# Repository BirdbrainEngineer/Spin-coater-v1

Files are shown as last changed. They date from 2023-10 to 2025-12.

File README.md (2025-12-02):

# Birbrain's DIY Spin Coater version 1
This repository contains the source code for a diy spin coater I designed. A video on YouTube showing some of the design- and build process of this device can be found [here](https://www.youtube.com/watch?v=mm2ZiJNfISs). 

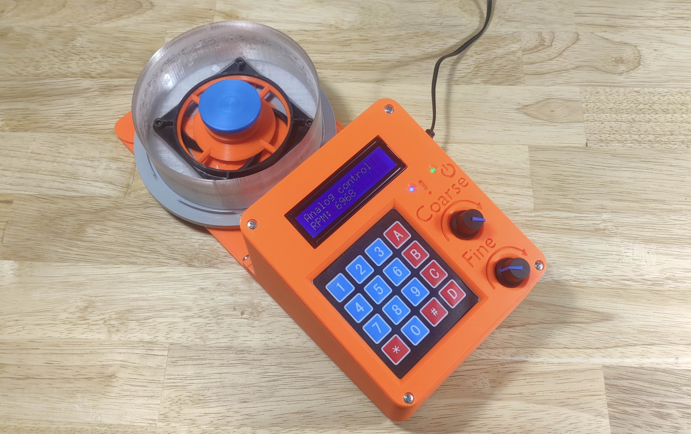
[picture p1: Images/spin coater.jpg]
Birdbrain's DIY Spin Coater version 1


### What is it?
 A spin coater is a tool used for depositing thin films of liquids onto a substrate. Usually the liquid is a solution of a relatively quickly evaporating solvent and the coating solute. The phantom force of centrifugal force causes any liquids to travel radially outwards on the substrate. However, due to surface tension, viscocity and other phenomena, some of the solution sticks to the substrate. The solvent from the thin layer of solution then evaporates, leaving behind a thin film of the solute. Using this technique, it is possible to obtain film thicknesses as small as a couple-dozen nanometers!
 
  So... in a nutshell, a spin coater is essentially just a controllable/programmable spinner onto which one can attach a variety of substrates. 
 
### Why?
 Due to the insane simplicity of this device, one would imagine that such tools would be rather cheap and easy to aquire... However, because usually these devices are used in universities and research laboratories, then unfortunately one can expect a markup in the hundreds, to sometimes thousands of percentage points!!! This is just pure insanity, and because I like building some of my own tools, I decided to design and build my own simple spin coater.

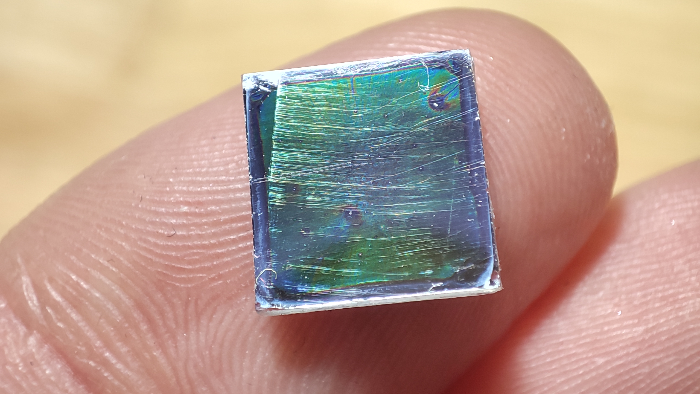
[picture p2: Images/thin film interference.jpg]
Thin film interference
 
 Above is a photo showing thin-film-interference on a coated first-surface mirror(definitely not optical quality haha). The coating solvent was acetone and solute was acrylic, which is a very challenging mix to work with... hence the somewhat sub-par result. 

### Is this project going to be maintained? 
 Don't hold your breath for it! I may upload a few bug fixes if and when they pop up as I work with my spin coater, but I do not intend to improve this version much if at all. There is a likelyhood that a few years from now, I will build a yet more advanced version- a spin coater of laboratory quality for projects that require utmost precision. 

### What is needed to build this project?
The spinner hardware is controlled by a Raspberry-Pi Pico(just Pico from here on), a cheap microcontroller that sits between an Arduino and ESP32 in its processing power. The speed of the Pico as well as its powerful hardware-PWM capabilities are the reason for me picking the Pico for this project.

Multiple extremely important parts of the device, such as the hub and sample holder combo that makes up the gravity chuck design of this spin coater, are meant to be 3d-printed. So, it is basically a necessity to have access to a basic 3d printer... or a cnc mill if going overkill. 

Because I did not make a PCB design for the logic board for this project, then you'll also need access to a soldering station.

And of course, a PC of some sort to be able to compile- and upload the firmware onto the Pico. More on software at [software setup](#software-setup) paragraph of this document.

The list of parts along with their approximate cost can be found at [bill of materials](#bill-of-materials) section of this document. 

## Software setup
This project uses [PlatformIO](https://platformio.org/) with [Visual Studio Code](https://code.visualstudio.com/)(VSCode) IDE. This near-trivializes certain aspects of programming for the Pico. In addition, this project uses the "earlephilhower" Arduino-pico core (see platformio.ini). For these reasons, as far as I am aware, the code is not possible to compile with any other setup, and even if it is possible, I recommend VSCode with PlatformIO anyways. Because the code uses a couple external libraries that PlatformIO normally manages, then it is necessary to have an Internet connection while dealing with this code. 

Getting the firmware for the Pico running should be as simple as these three steps. 

1. Clone the repository to your desired location and open the project in VSCode.
2. Connect the pico to your machine over a usb cable, while holding down the "BOOTSEL" button on the Pico. Release the BOOTSEL button after the Pico is connected.
3. Click "Build" and then "Upload" in VSCode, or just "Upload"(this should automatically build the project). The firmware should then be compiled and uploaded to the Pico. Once VSCode signals to you that the upload is complete, simply unplug the USB from the Pico and on the next power-up of the Pico, it should execute the code of the firmware.

Granted that the rest of the surrounding hardware has been built and set up correctly, the spin coater should just simply work. Surrounding hardware specification can be found under the "[Hardware design](#hardware-design)" paragraph of this document.

## Bill of materials
The prices in the bill of materials are approximate prices of the components that I could quickly find at the time of publishing of this document. These prices are most certainly subject to change over time.

* Anything in brackets is the particular size/component I used.
* Price is for the full amount (eg. 2$ for a component that has 4 stated in the amount, means each component costs 0.50$). 

| Amount | Component                                    | Price  |
|--------|----------------------------------------------|--------|
| 1      | Raspberry Pi Pico                            | 5$     |
| 1      | 80mm 4-pin PC fan (Arctic P8 Max)            | 10$    |
| 1      | 12V, 1A, power adapter with barrel connector | 5$     |
| 1      | SPI micro-SD-card reader module              | 3$     |
| 1      | 16x2 LCD display module                      | 4$     |
| 1      | 4x4 membrane keypad                          | 5$     |
| 1      | 15x21mm KCD1 power switch                    | 1$     |
| 1      | Suitable DC-005 barrel jack (5.5x2.1mm)      | 1$     |
| 4      | Suitable anti-slip rubber furniture leg      | 2$     |
| 1      | 25x (empty) cd/dvd spindle                   | 3$/10$ |
| 2      | WH148 10K potentiometer                      | 2$     |
| 2      | WH148 potentiometer knob                     | 2$     |
| 2      | PT15 10K potentiometer or equivalent         | 0.50$  |
| 12     | 3mm M3 heat set insert                       | 1$     |
| 4      | 4mm M4 heat set insert                       | 1$     |
| 2      | TO220 heatsinks                              | 1$     |
| 16     | M3 10mm screw                                | 0.50$  |
| 4      | M4 20mm or 17mm screw*                       | 0.50$  |
| 1      | 12x8cm prototyping/perf board                | 0.50$  |
| 1      | 1A glass tube fuse                           | 0.50$  |
| 1      | glass tube fuse holder                       | 0.50$  |
| 1      | 1N5819 schottky diode or equivalent          | 0.50$  |
| 5      | 1N4005 diode or equivalent                   | 1$     |
| 2      | 3mm round LED, different colors              | 0.50$  |
| 6      | resistors: 1x1K, 1x4K7, 1x6K8, 2x10K, 1x68K  | 0.50$  |
| 4      | 100nF ceramic capacitor                      | 0.50$  |
| 1      | 330nF 15V+ capacitor(I used 1x100nF, 1x100uF)| 0.50$  |
| 2      | 100uF 15V+ electrolytic capacitor            | 0.50$  |
| 2      | 2N2222A transistor or equivalent             | 0.50$  |
| 1      | F9540N transistor or equivalent              | 1$     |
| 1      | L7805CV voltage regulator                    | 1$     |
| -      | Preferred connectors & wiring for soldering  | ~5$    |
| -      | ~235g of PLA filament                        | 7$     |
| -      | ~42g of PETG filament                        | 1.50$  |

* Total: ~69$

## Hardware design
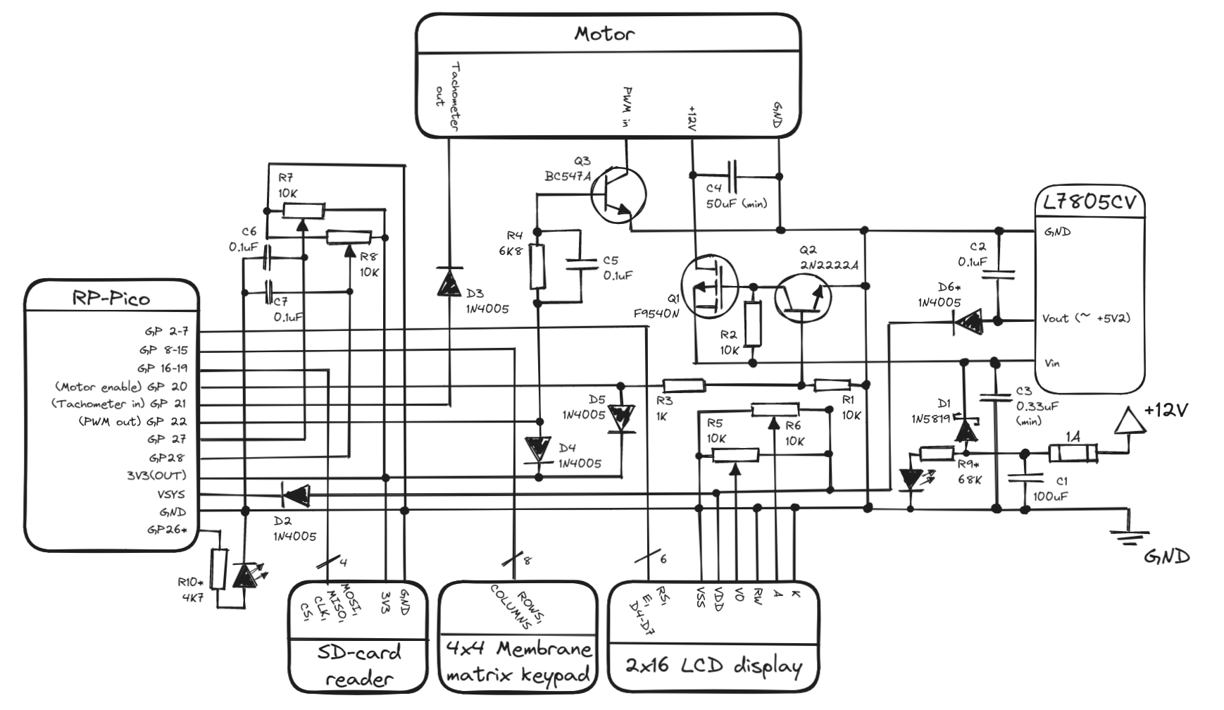
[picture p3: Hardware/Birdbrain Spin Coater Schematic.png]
Schematic


* Parts with a "*" are technically optional, but recommended. LED-s following a resistor with a * are optional in the same manner. 
* Q3 transistor in the schematic is a BC547A, however this can be replaced with a 2N2222A or equivalent. BC547A is an old and deprecated NPN BJT. The reason why I used it is to have a slower signal fall time (yes, really), which helps to make the PWM duty-cycle look more like what the Pico outputs. With a 2N2222A transistor, the PWM duty cycle to the fan motor is shorter than what the Pico outputs. Technically it should be fine as the PID control loop should be able to compensate.
* R5 & R6 are PT15 type potentiometers. R7 & R8 are WH148 type potentiometers.
* All 1N4005 diodes could technically be replaced by 1N5819 schottky diodes, but should not be necessary. 
* C3 capacity comes from the datasheet for L7805CV, however it does appear that the capacity can be larger. Probably the more important thing is that at least some of the capacity is quick-acting, eg. ceramic capacitors. 

### Some notes on the design...
If you would prefer to use a KiCAD schematic, then one has been produced and tested by @krasimirk. It can be found in the [BirdbrainSpinCoaterPCB_v1.1 directory](Hardware/BirdbrainSpinCoaterPCB_v1.1).

Make sure to install a TO-220 heatsink at least on the L7805CV, it will burn out otherwise. A heatsink on the F9540N is technically not needed, but optional.

One might notice that the 16x2 LCD display is directly interfaced with the Pico, even though the LCD display is running off 5V. This is safe to do as long as RW is tied to ground, guaranteeing that the display only ever gets written to. In such a case, the Pico's 3.3V should be enough to count as a logical high while transmitting data. 

## Spinner usage
If you have built yourself a spin coater of this design and firmware then here's a rundown of what can be found in the menu system of the spinner and what the different options do. 

### Keys
By default the keymapping for the spin coater when using the default 4x4 membrane keypad is as follows:

* Numerics - Correspond to the corresponding number. 
* `*` - Backspace / Exit.
* `#` - Enter / OK.
* `A` - YES, if a question prompt appears; Otherwise the letter A.
* `B` - NO, if a question prompt appears; Otherwise the letter B.
* `C` - UP, if navigating the menus; Otherwise the letter C.
* `D` - DOWN, if navigating the menus; Decimal dot/period ( `.` ), if entering a fractional number; Otherwise the letter D. 

### Booting
*For a painless first boot of the spin coater, make sure to copy the contents of the "Spinner Memory Image" folder onto a clean SD card. Ideally the SD card has a relatively small memory size.*

During booting, the spin coater checks for whether an SD card can be found on the default SPI pins. If not, then the spin coater will enter [memoryless operation](#memoryless-operation), and notifies the user of this occuring. The menu should then appear and the spin coater is ready for use in memoryless operation mode. 

If the SD card is present, then next the spin coater will check whether a `JOBS` folder exists in the root directory of the SD card. If not, one will be created automatically. If the `JOBS` folder exists, then the spin coater will attempt to load any jobs in the folder. The `JOBS` folder should contain *only* job files. [Job files](#job-file-structure) are extensionless JSON files with a very specific structure. Errors during this phase of booting could end up being unrecoverable AND recurring. If this is the case, the spin coater should be shut down, after which the SD card has to be removed from the spin coater and the files inspected at a PC. Any job files that have been saved incorrectly should be deleted from the folder. The spin coater should be able to boot again after doing so. 

Next the spin coater will attempt to locate the PID test job file called `PID` in the root directory. If this job is not found or is corrupted, then the spin coater will not be able to use the "PID test" functionality. In case of this happening and the user still wanting to use the PID test functionality, the user should shut down the spin coater, then remove the SD card from the spin coater and inspect the files at a PC. If a file called `PID` exists in the root directory then the integrity of the file should be checked, or alternatively a new PID test job file should replace the corrupted one. If the file is missing then a job has to be created/copied, and the file renamed to `PID`. 

### Normal operation
* `1/5: Quick start`
    * `1/2: Programmed` - Opens up a standard [job routine creation](#job-routine-creation) dialouge. After the dialouge has been finished, asks whether to run the job or not. If answered affirmatively, then executes the programmed job routine. After the routine has finished, asks whether to run the job again or not. If answered affirmatively, runs the job again. Otherwise asks whether to store the job permanently. If answered affirmatively, then a job name can be entered and the job routine will be saved as a job that can be interacted with through the `Jobs` menu.  
    * `2/2: Analog` - Gives direct control over the spinner to the user. The speed can be adjusted using the "coarse" and "fine" potentiometers. Coarse control spans from 0% to 90% of maximum spinner speed. Fine control spans a 10% range that gets added ontop of the current coarse control. Eg. if coarse control is set to 38% and fine control to 4%, then the output speed will be 42% of the maximum spinner speed. **WARNING: When exiting analog control mode, the spinner spins up to a slow speed for a few seconds, even if the spinner is already stationary!**
* `2/5: Jobs`
    * `1/3: Load job` - Opens a list of jobs currently stored on the SD card. The specific job can be searched in the menu, or by using the `Search for a job` function. If the job search turns up positive or the specific job is chosen from the menu, the spin coater asks whether to run the job. If answered affirmatively, performs the job routine. 
    * `2/3: Create job` - First asks to enter the new job routine's name. If a job with the specified name already exists, then offers to enter a different name or delete the job with the specified name. Once a suitable name is chosen, the spin coater asks to confirm the name, after which the standard [job routine creation](#job-routine-creation) dialouge is opened. After the job routine is finished, the job is saved on the SD card. If the user decided to override a previous job, then the previous job with the same name is deleted before the new job is saved. 
    * `3/3: Delete job` - Opens a list of jobs stored on the SD card. The specific job the user wishes to delete can be searched in the menu, or by using the `Search for a job` function. When answered affirmatively to whether to really delete the specified job, the job is removed deleted from the SD card. **As it stands right now, the "Search for a job" option is rather buggy, so it is not recommended to use it!**
* `3/5: Test`
    * `1/2: Spinner params.` - Spinner parameters test is a rudimentary test to find out some basic parameters of the spinner. The test consists of a speed- and acceleration tests. The speed test finds out the minimum and maximum speed of the spinner, as well as the minimum duty cycle length to make the spinner spin. The acceleration test tests the maximum acceleration and deceleration three times in a row, and then averages the results. The results from the tests are then displayed to the user to create their job routines accordingly. The minimum duty cycle speed will not be reported to the user but the spin coater's configuration is updated accordingly. **Please note that since the very first test is finding out the minimum duty cycle of the spinner, it may look like nothing is happening for a while. Rest assured, the controller is simply creeping up on the minimum duty cycle.**
    * `2/2: PID` - PID test is a rudimentary test to gauge whether the current PID constants are performing acceptably. The routine of this test can be changed by manually replacing the job file named `PID` in the root directory on the SD card. 
* `4/5: Calibration`
    * `1/6: Set Kp` - Displays the currently set P (proportional) constant of the PID controller. If no numeric value is entered, the constant remains unchanged, otherwise new number is set as the new value of the constant. The configuration of the spin coater is also updated so on next "normal operation" boot the constant is retained. 
    * `2/6: Set Ki` - Displays the currently set I (integral) constant of the PID controller. If no numeric value is entered, the constant remains unchanged, otherwise new number is set as the new value of the constant. The configuration of the spin coater is also updated so on next "normal operation" boot the constant is retained. 
    * `3/6: Set Kd` - Displays the currently set D (derivative) constant of the PID controller. If no numeric value is entered, the constant remains unchanged, otherwise new number is set as the new value of the constant. The configuration of the spin coater is also updated so on next "normal operation" boot the constant is retained. 
    * `4/6: Min duty cycle` - Updates the configuration of the spin coater to reflect the new minimum duty cycle value obtained during the last "Spinner parameters" test. Effect is immediate.
    * `5/6: Analog-in alpha` - Allows for adjusting the alpha of the exponential average for the analog control potentiometer readings. Should be a value between `0` and `1` (default is `0.01`). Smaller values mean the average, and therefore the whole reading of the potentiometers moves slower, but noise in the readings is suppressed. **Changing this value is unlikely to be needed.**
    * `6/6 RPM alpha` - Allows for adjusting the alpha of the exponential average for the RPM readings. Should be a value between `0` and `1`(default is `0.2`). Smaller values mean the average, and therefore the whole reading of the potentiometers moves slower, but noise in the readings is suppressed. **Changing this value is unlikely to be needed.**
* `5/5: Information`
    * `1/3: Device info.` - Device information contains the current revision of the firmware and hardware, programmer names/handles and hardware developer names/handles, as well as the software- and hardware license identifiers.
    * `2/3: HARDWARE LICENSE` - Embedded license identifier and link for more information about the Creative Commons 4.0 Attribution-ShareAlike license.
    * `3/3: SOFTWARE LICENSE` - Embedded MIT license.

### Memoryless operation
In memoryless operation mode the spin coater is not able to execute any functionality that has to do with accessing the memory, naturally. 

If `Programmed` is chosen from first menu option `Quick start`, then the spin coater will not offer to save the created set of instructions as a job when exiting the `Programmed` mode. 

The second menu option `Jobs` is completely non-functional. 

The "PID test" under third menu option `Test` is not available.

All spinner configuration will have reverted back to firmware defaults. It is possible to update the configuration, however if the spin coater is shut down, all changes made are lost.

## Building your own
If you would like to build your own spin coater of this design, then the [assembly manual](https://birdbrain.engineer/spin-coater/instructions/) can be found in the **Instructions** folder of this repository.

## Licenses
The software of this project is licensed under [MIT](https://opensource.org/license/mit/) software license.

The hardware design of this project is licensed under [Creative Commons 4.0 Attribution-ShareAlike](https://creativecommons.org/licenses/by-sa/4.0/deed.en) license.

## Job routine creation

When creating a job routine in the spinner, the spinner will ask the following three questions in a loop.

1. **Which task to perform** 
    
    * *Ramp* - Performs a linear ramp-up or ramp-down of the speed of the spinner.
    * *Hold* - Holds the spinner speed at a specified speed.
    * *End* - Final instruction in a job routine, if this is encountered, the job routine is immediately stopped and finished.

2. **RPM / Speed**
    
    If the task was to "ramp", then it will linearly interpolate towards this speed from the previously set speed (0 if first task in the routine). If the task was "hold", then sets the speed setpoint to this speed. No effect if any other task is encountered.

3. **Duration**

    The duration of the particular task in the routine in **milliseconds**. In case of "ramp" task, the speed is interpolated over the course of this time duration. In case of "hold" task, the speed is set and held for this time duration. No effect if any other task is encountered.

Once the `End` task is chosen while programming a job routine, the spin coater will immediately assume the job routine finished and so the programming interface is exited.

For example, if the following commands are entered while programming:

* Ramp, 3000, 5000
* Hold, 3000, 5000
* Ramp, 500, 6000
* End

... then when the job gets executed, the spin coater would linearly spin the spinner from 0 RPM up to 3000RPM over the course of 5 seconds. It would then hold the speed at 3000RPM for a further 5 seconds. Finally, it would linearly slow down the spinner from 3000RPM to 500RPM over the course of 6 seconds. The job would then immediately finish. 

## Job file structure
Job files are [JSON](https://www.json.org/json-en.html) files with no `.json` extension.

To have the spin coater load your job files, they need to be placed into the `JOBS` folder which should be found in the root directory of the SD card. The only exception to this is the job file called `PID`, which is used for the PID test. The `PID` job should be found in the root directory of the SD card.

The following is a sample job file.

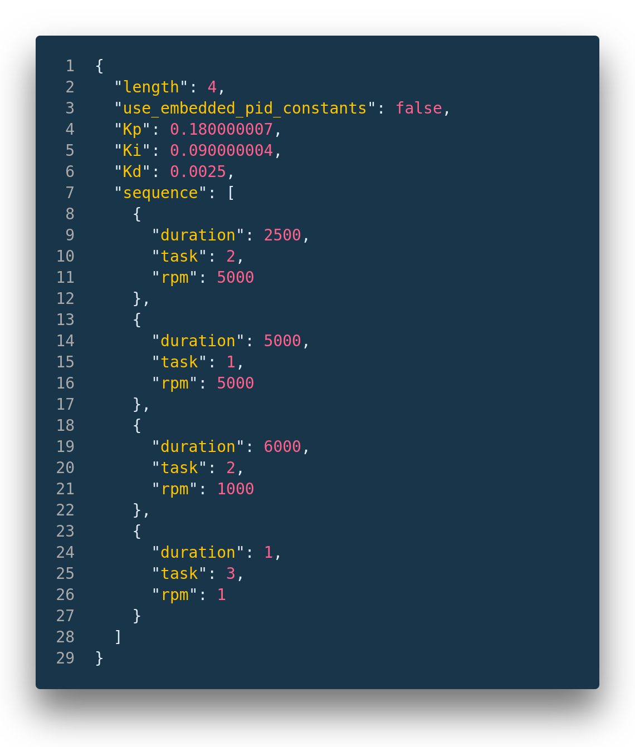
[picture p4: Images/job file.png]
Sample structure of a job file


The job file has 5 single-valued variables and a single array.

* `length` is an integer that **must** be equal to the number of elements in the `sequence` array.
* `use_embedded_pid_constants` is a boolean which specifies whether to use the `Kp`, `Ki` and `Kd` values baked into the job file as PID constants for the PID controller, or whether to use the spinner's currently set internal PID constants. `false` means that the spinner's internal PID constants are used instead of the constants specified in the file.
* `Kp` is a floating point number that will be used as the **Kp** constant for the PID controller if `use_embedded_pid_constants` is set to `true`. 
* `Ki` is a floating point number that will be used as the **Ki** constant for the PID controller if `use_embedded_pid_constants` is set to `true`. 
* `Kd` is a floating point number that will be used as the **Kd** constant for the PID controller if `use_embedded_pid_constants` is set to `true`. 
* `sequence` is an array type which holds elements made of three variables:
    * `duration` is an integer. Refer to [job routine creation](#job-routine-creation) for more information.
    * `task` is an integer. `1` means "hold" task, `2` means "ramp" task and `3` means "end" task. No other numbers should be used here. Refer to [job routine creation](#job-routine-creation) for more information.
    * `rpm` is an integer. Refer to [job routine creation](#job-routine-creation) for more information.

## Known bugs
* The `Search for a job` functionality under `Delete job` menu does not work properly if the name contains numbers. **Workaround:** Find the job you wish to delete in the `Delete job` menu manually and delete it that way.

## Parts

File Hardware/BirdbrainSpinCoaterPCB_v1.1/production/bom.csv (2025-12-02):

Designator | Footprint | Quantity | Value | LCSC Part #
C1 | CP_Radial_D5.0mm_P2.00mm | 1 | 100u
C2, C5, C6, C7 | DualFootprint_C1206_Radial | 4 | 0.1u
C3 | DualFootprint_C1206_Radial | 1 | 0.33u
C4 | CP_Radial_D5.0mm_P2.00mm | 1 | 50u
D1 | D_DO-41_SOD81_SOD123_P10.16mm_Horizontal | 1 | 1N5819
D2, D3, D4, D5, D6 | D_DO-41_SOD81_SOD123_P10.16mm_Horizontal | 5 | 1N4005
D7, D8 | LED_D5.0mm | 2 | LED
F1 | Fuseholder_Clip-5x20mm_Littelfuse_100_Inline_P20.50x4.60mm_D1.30mm_Horizontal | 1 | Fuse
F2 | 1210 | 1 | Fuse
J1 | PinHeader_1x08_P2.54mm_Vertical | 1 | Keyboard
J2, J5, J6 | PinHeader_1x06_P2.54mm_Vertical | 3 | SD-Card Reader
J3 | PinHeader_1x16_P2.54mm_Vertical | 1 | LCD Display
J4 | TerminalBlock_Phoenix_MKDS-1,5-2-5.08_1x02_P5.08mm_Horizontal | 1 | PowerConnector
M1 | PinHeader_1x04_P2.54mm_Vertical | 1 | Fan_4pin
Q1 | TO-220-3_Vertical | 1 | IRF9540N
Q2 | TO-92_Dual | 1 | BC547
Q3 | TO-92_Dual | 1 | PN2222A
R1, R2 | DualFootprint_R1206_Axial7.62 | 2 | 10K
R10 | DualFootprint_R1206_Axial7.62 | 1 | 4K7
R3 | DualFootprint_R1206_Axial7.62 | 1 | 1K
R4 | DualFootprint_R1206_Axial7.62 | 1 | 6K8
R5, R6, R7, R8 | Potentiometer_Bourns_3296W_Vertical | 4 | 10K
R9 | DualFootprint_R1206_Axial7.62 | 1 | 68K
TP1, TP2, TP3 | PinHeader_1x01_P2.54mm_Vertical | 3 | GND
TP4 | PinHeader_1x01_P2.54mm_Vertical | 1 | 12V FAN
TP5 | PinHeader_1x01_P2.54mm_Vertical | 1 | TM
TP6 | PinHeader_1x01_P2.54mm_Vertical | 1 | PWM
TP7 | PinHeader_1x01_P2.54mm_Vertical | 1 | 5V
U1 | RPi_Pico_SMD_TH | 1 | Pico
U2 | TO-220-3_Vertical | 1 | LM7805

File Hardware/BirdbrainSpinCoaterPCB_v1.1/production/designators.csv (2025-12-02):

C1:1
C2:1
C3:1
C4:1
C5:1
C6:1
C7:1
D1:1
D2:1
D3:1
D4:1
D5:1
D6:1
D7:1
D8:1
F1:1
F2:1
H1:1
H2:1
H3:1
H4:1
J1:1
J2:1
J3:1
J4:1
J5:1
J6:1
M1:1
Q1:1
Q2:1
Q3:1
R1:1
R10:1
R2:1
R3:1
R4:1
R5:1
R6:1
R7:1
R8:1
R9:1
TP1:1
TP2:1
TP3:1
TP4:1
TP5:1
TP6:1
TP7:1
U1:1
U2:1

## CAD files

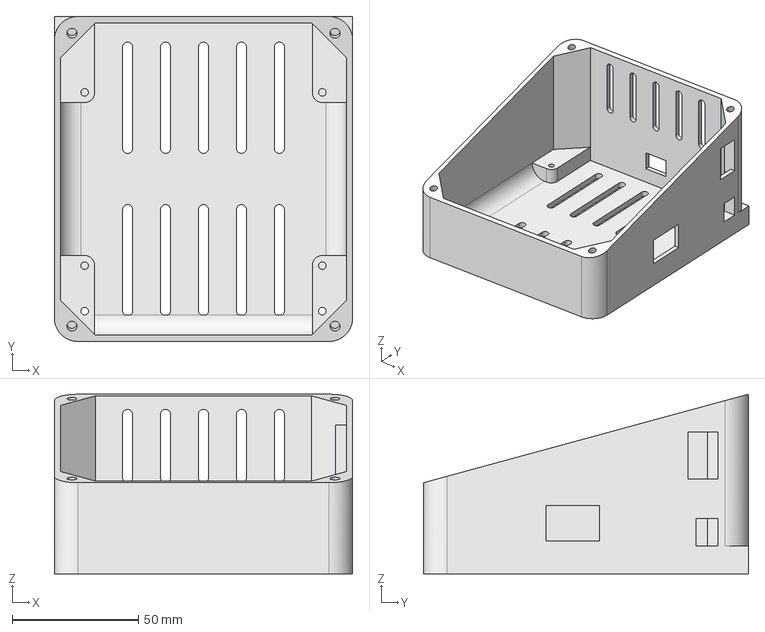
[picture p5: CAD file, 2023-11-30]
Hardware/freecad/chassis.FCStd
118.0 x 128.5 x 71.0 mm

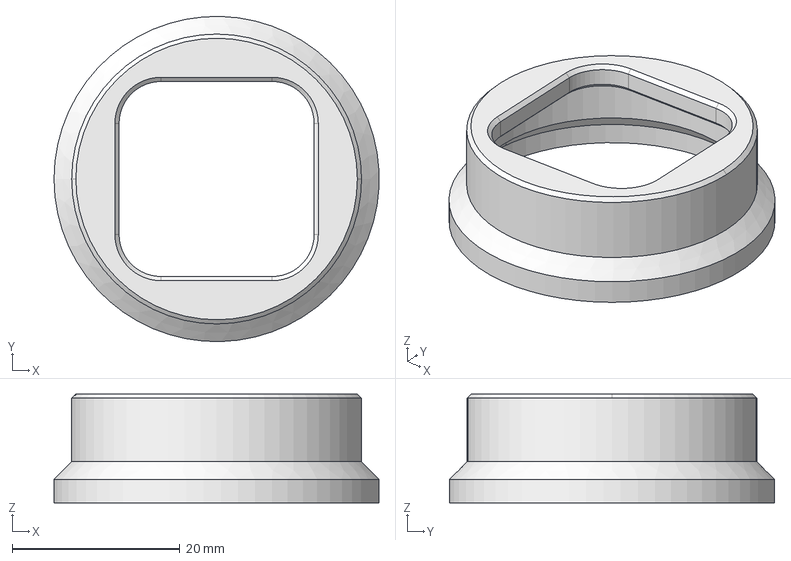
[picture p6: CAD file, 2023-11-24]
Hardware/freecad/spin coater hub.FCStd
38.8 x 38.8 x 13.0 mm

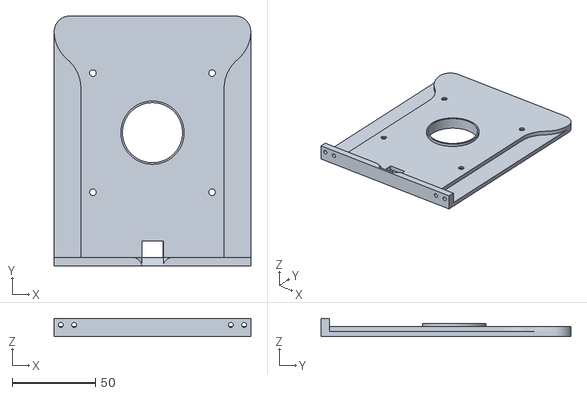
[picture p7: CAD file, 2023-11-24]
Hardware/stl/chassis_1.stl
118.0 x 150.0 x 11.0

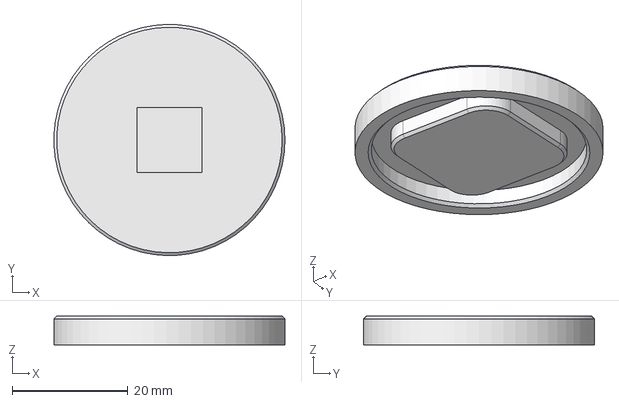
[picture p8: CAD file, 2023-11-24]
Hardware/freecad/sample holder.FCStd
40.0 x 40.0 x 5.00 mm

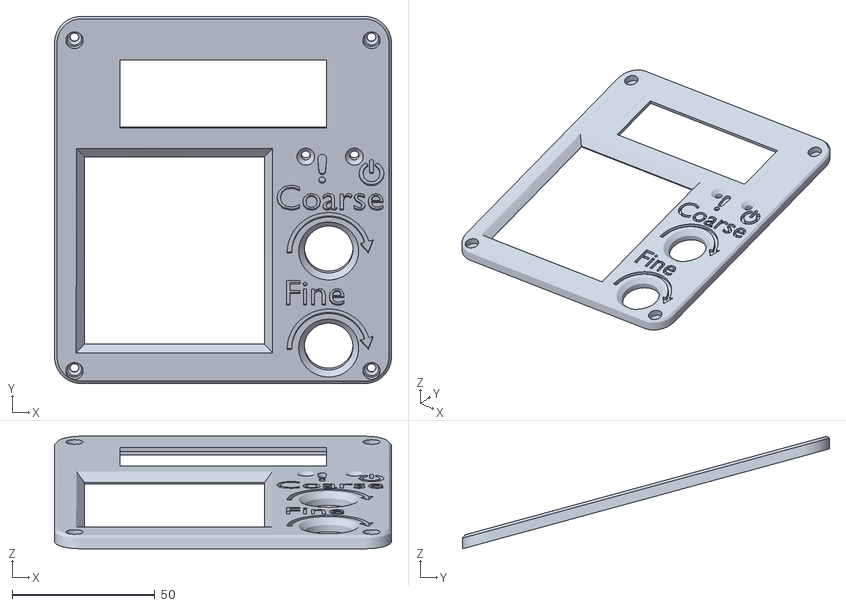
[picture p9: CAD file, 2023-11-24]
Hardware/stl/chassis_3.stl
118.0 x 128.5 x 39.4

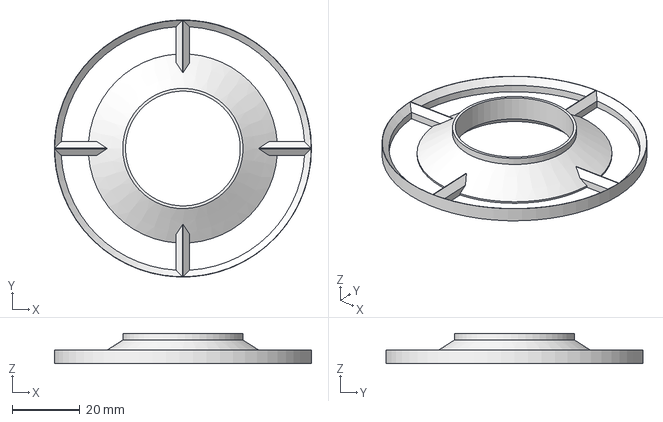
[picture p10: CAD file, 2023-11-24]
Hardware/freecad/spin coater skirt.FCStd
76.1 x 76.1 x 9.00 mm

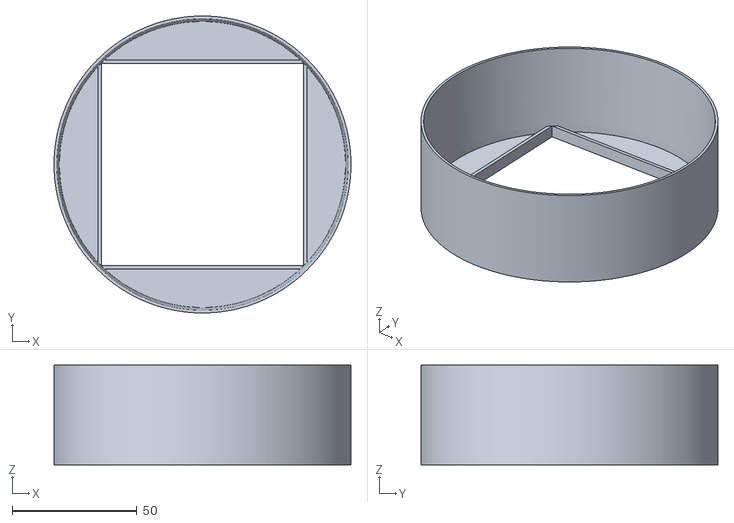
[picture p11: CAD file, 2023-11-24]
Hardware/stl/spray catcher.stl
119.0 x 119.0 x 40.0

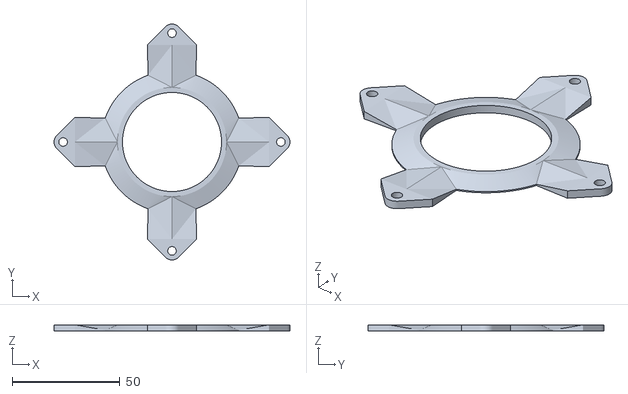
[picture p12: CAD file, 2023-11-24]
Hardware/stl/mount.stl
109.6 x 109.6 x 3.00

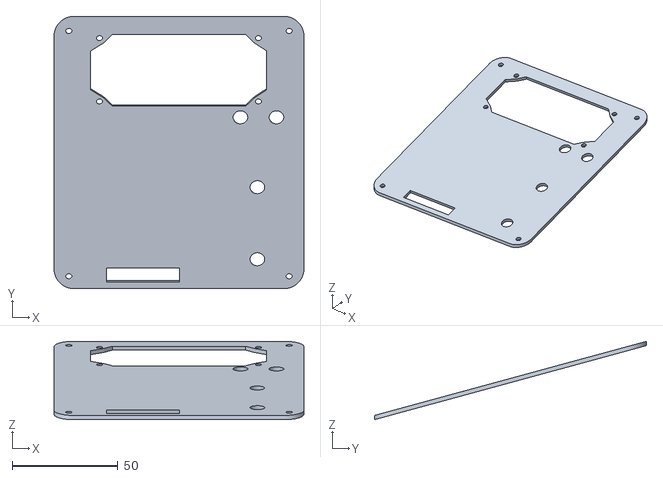
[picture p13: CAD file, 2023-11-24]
Hardware/stl/chassis_2.stl
118.0 x 128.5 x 37.0

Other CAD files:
Hardware/stl/chassis_0.stl
Hardware/stl/sample holder example.stl
Hardware/stl/skirt.stl
Hardware/stl/hub.stl

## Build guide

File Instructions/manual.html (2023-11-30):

# Birdbrain's Spin Coater version 1 assembly manual

## Foreword

Welcome to the assembly manual for "Birdbrain's Spin Coater v1". A video showcasing the author's build of the device as well as working principle can be found on YouTube (https://www.youtube.com/watch?v=mm2ZiJNfISs).

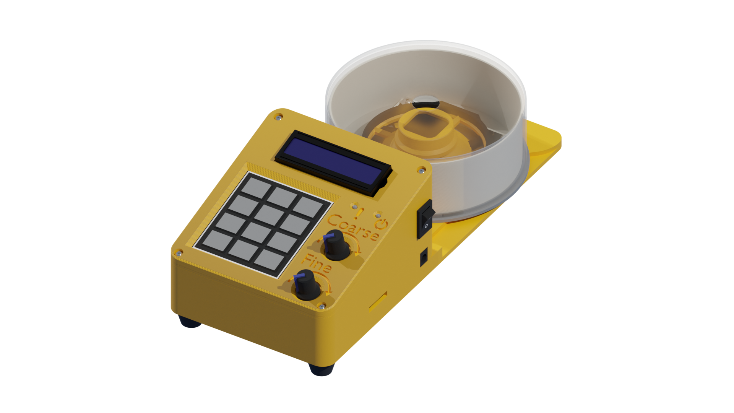
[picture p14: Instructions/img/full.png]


A spin coater is a tool used for depositing very thin films of liquids onto a solid substrate. Depending on the characteristics of the liquid, the films can be as thin as a couple dozen nanometers thick. Often the liquid is a solution of some sort, eg. photoresists. The liquid solution is spin coated, after which the solvent is allowed to evaporate (sometimes actively driven off with the application of heat), leaving behind a thin film of the desired solute.

These devices are often found used in universities, research laboratories and specialized manufacturing facilities, eg. integrated circuit fabs. For that reason, these devices are often overly expensive for what they are - essentially just a programmable spinner. The author did not want to spend thousands of $ on such a device and so decided to make a basic version of their own for a tiny fraction of the cost of buying one.

## What you will need

The manual at hand uses the metric system for its measurements with the default unit being millimeters (mm).

To successfully replicate this project you will require some tools, which are listed below.

- 3D printer*
- Soldering station
- Personal computer
- Drill with various bits
- Saw (metal saw works great)
- Screwdriver compatible with your chosen screws
- Small file(s)
- Craft knife
- Hot glue gun or superglue
- Wire strippers and/or crimping tool(s)**

*

FDM or SLA printer both work. Alternatively, a CNC mill if you are extremely adventurous - requires modifying .stl files to fit your needs.

**

First 3D print out the parts in .stl files, which can be found in the Hardware folder of the project's GitHub repository (https://github.com/BirdbrainEngineer/Spin-coater-v1). Required prints are chassis_0.stl, chassis_1.stl, chassis_2.stl, chassis_4.stl, skirt.stl, hub.stl. Additional optional prints are mount.stl, spray catcher.stl.

Comprehensive list of required components

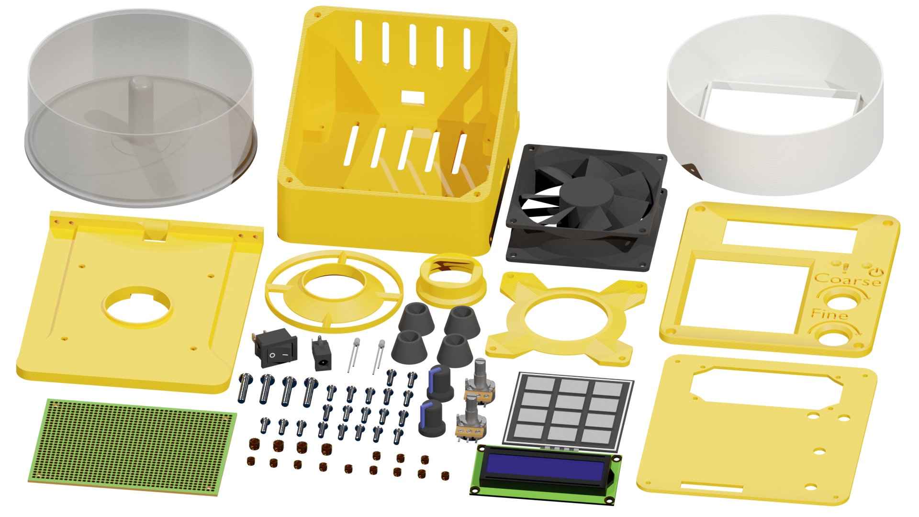
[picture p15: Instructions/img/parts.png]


*Parts used to make the logic board not shown here but listed below

- 1x Chassis_0 part
- 1x Chassis_1 part
- 1x Chassis_2 part
- 1x Chassis_3 part
- 1x Skirt part
- 1x Hub part
- 1x Mount part *(0)
- 1x Spray catcher part *(0)
- 1x Raspberry Pi Pico
- 1x 80mm 4-pin PC fan (high speed better)
- 1x 12V, 1A, power adapter with barrel connector
- 1x SPI micro-SD-card reader module
- 1x 16x2 LCD display module
- 1x 4x4 membrane matrix keypad
- 1x 15x21mm KCD1 power switch
- 1x Suitable DC-005 barrel jack (depends on your power adapter)
- 4x Anti-slip rubber furniture leg with M3 hole
- 1x 25x (empty) cd/dvd spindle
- 2x WH148 10K potentiometer
- 2x WH148 potentiometer knob
- 2x PT15 10K potentiometer or equivalent
- 12x 3mm M3 heat set insert
- 4x 4mm M4 heat set insert
- 2x TO220 heatsinks *(1)
- 16x M3x10mm screw
- 4x M4x20mm or x17mm screw *(2)
- 1x 12x8cm prototyping/perf board
- 1x 1A glass tube fuse
- 1x glass tube fuse holder
- 1x 1N5819 schottky diode or equivalent
- 5x 1N4005 diode or equivalent *(3)
- 2x 3mm round LED, different colors *(0)
- 1x 1K resistor
- 1x 4K7 resistor *(0)
- 1x 6K8 resistor
- 2x 10K resistor
- 1x 68K resistor *(0)
- 4x 100nF ceramic capacitor
- 1x 330nF 15V+ capacitor
- 2x 2N2222A transistor or equivalent *(4)
- 1x F9540N transistor or equivalent
- 1x L7805CV voltage regulator
- Preferred wires and connectors

*(0)

Optional but recommended

*(1)

Only 1 is strictly required, second one optional

*(2)

Use 20mm screw if "mount" part is used, 17mm otherwise

*(3)

One diode is optional

*(4)

Q3 on schematic is BC547A, but is assumed to be 2N2222A instead

Depending on your proficiency with soldering diy prototype boards, set aside around 3 to 9 hours for soldering alone. The rest of the assembly should take around 30 minutes to an hour.

## 1. Logic board

Parts and tools needed

- 1x 12x8cm prototyping/perf board
- 1x Raspberry Pi Pico
- 1x SPI micro-SD-card reader module
- 2x TO220 heatsinks
- 1x 1A glass tube fuse
- 1x glass tube fuse holder
- 1x 1N5819 schottky diode or equivalent
- 5x 1N4005 diode or equivalent
- 1x 1K resistor
- 1x 4K7 resistor
- 1x 6K8 resistor
- 2x 10K resistor
- 1x 68K resistor
- 4x 100nF ceramic capacitor
- 1x 330nF 15V+ capacitor
- 2x 2N2222A transistor or equivalent
- 1x F9540N transistor or equivalent
- 1x L7805CV voltage regulator
- Preferred wires and connectors
- Soldering station
- Craft knife

Because no PCB design exists for the logic board, it will be necessary to manually place and solder the components of the logic board onto a prototyping/perf board.

### Preparing the prototyping board

Take the 12cm x 8cm prototyping board and cut it to the required size of 10.5cm x 8cm (105x80 mm). To do this, use a Craft knife to cut out the "outline" of the board (best done straight along a row of holes). After which, you should be able to relatively easily break off the excess parts from the prototyping board.

Next drill 4 holes with a diameter of 3mm in the corners of the board. The distance between holes is shown below.

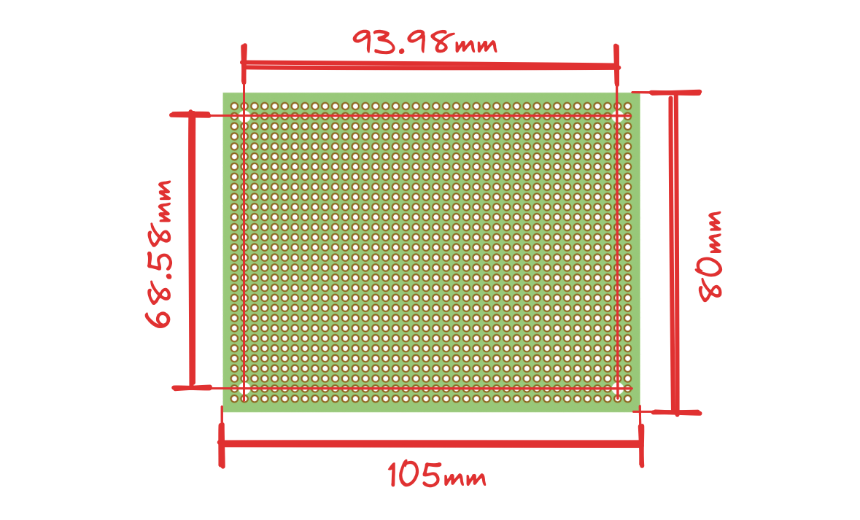
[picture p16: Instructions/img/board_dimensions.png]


### Soldering the logic board

Lay out the components on the prototyping board in whatever way you see most suitable to satisfy the logic board schematic below. The only hard requirement on placement concerns the "SPI SD card reader module" placement. The 6 pins connecting the SD card reader to the logic board (and the module) are designed to go exactly in the area indicated below, with the SD card slot pointing out of the board, naturally.

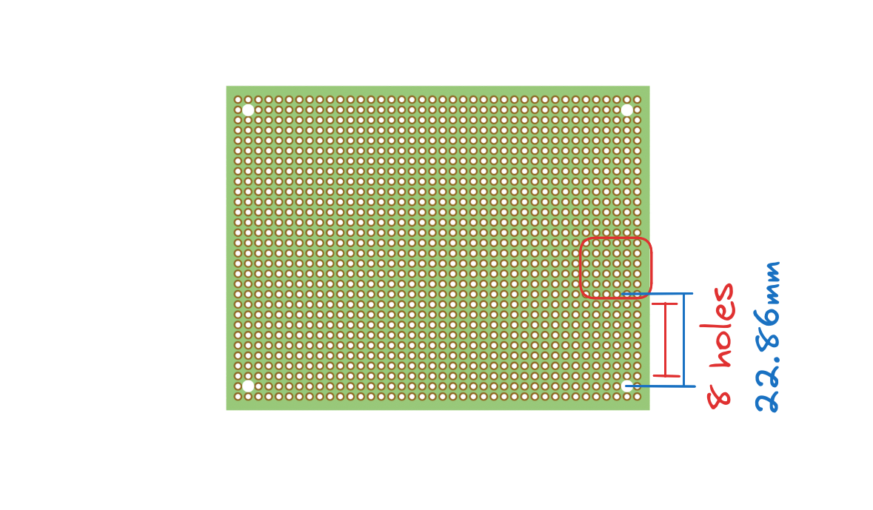
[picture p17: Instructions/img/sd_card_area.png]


Below is the logic board schematic



Do not solder the connection to the motor (4-pin fan), 4x4 matrix keybpad, 2x16 LCD display nor SD-card reader directly. There should be a connector of some sort to interface these devices with the logic board.

R7 and R8 should either be connected with ca. 100mm long wires, or better yet, with a connector.

R9 and R10 can be omitted, as long as the LED-s that follow them are also omitted. These LED-s should also be on ca. 100mm long wires or better yet, connect up with a connector.

Q3 can be replaced with a 2N2222A or equivalent transistor.

D6 is optional but recommended.

L7805CV requires a heatsink, otherwise it will get destroyed. While the F9540N transistor does not require a heatsink, it can be added.

It is also recommended to not solder the Raspberry Pi Pico directly to the prototyping board, but rather fashion a kind of socket for it, for example out of "0.1" female square header" parts.

Below is photos of how the author layed out and soldered their logic board.





Once you are done, you have yourself a Logic board part.

## 2. Spinner assembly

Parts needed

- 1x 80mm 4-pin PC fan
- 1x Hub
- 1x Skirt
- Saw
- Craft knife

The spinner assembly is the part of the spin coater that actually does the spinning. This project uses a 4-pin PC fan as a base for this purpose since a 4-pin PC fan has a lot of the necessary components for a programmable spinner already built into it - motor power commutation, electronic speed controller unit and tachometer.

### 1. Separate the fan's rotor and stator

There should be a retaining ring at the bottom of the PC fan. Remove it (don't break it! You will need it to reassemble the fan later!). After doing so, the rotor (the part with the fanblades) should simply slide out of the stator. Careful to not lose any springs, ball bearings and other parts that may have become loose. Make sure to take a note of how these parts were positioned as you will need to reassemble the fan later.

Note that the graphics shown in the manual do not show the stator's electromagnets, the author apologizes for this.

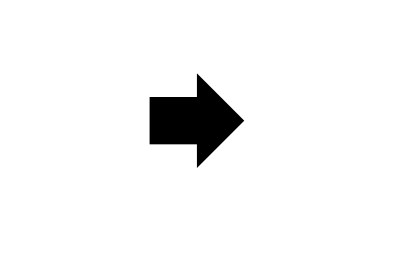
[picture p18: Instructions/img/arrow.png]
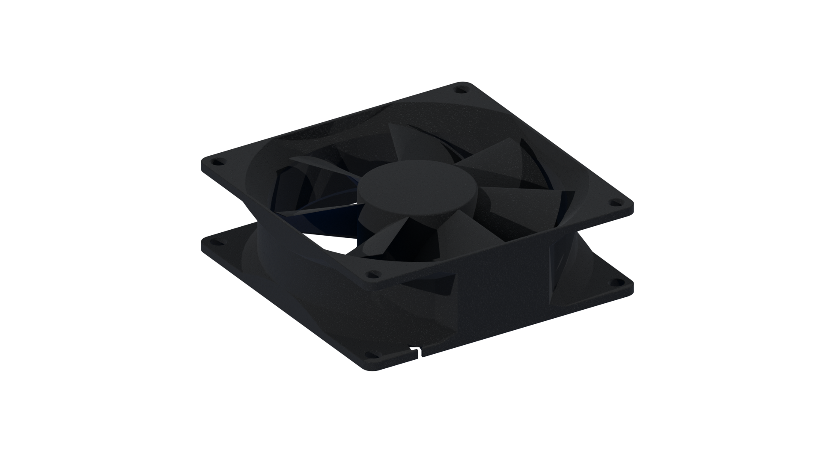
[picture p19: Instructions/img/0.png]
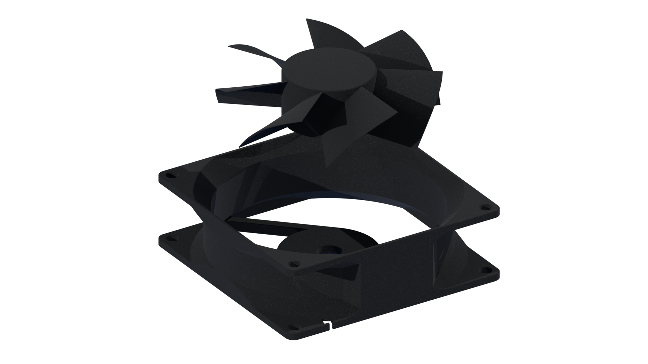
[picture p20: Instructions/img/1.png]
  

### 2. Remove fanblades

Break off the fanblades from the rotor. After that is done, use a craft knife to remove any protrusions left behind by the fanblades on the rotor - the sides of the rotor should be essentially smooth.

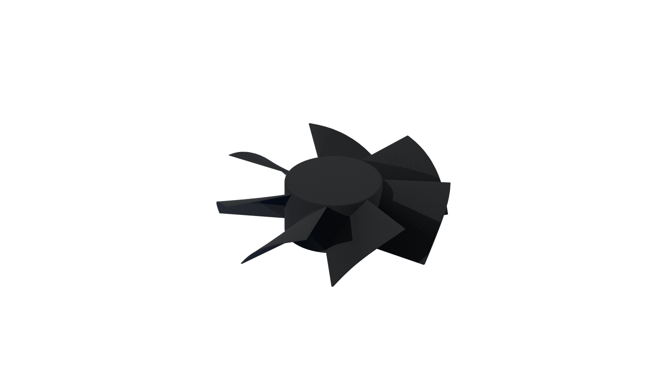
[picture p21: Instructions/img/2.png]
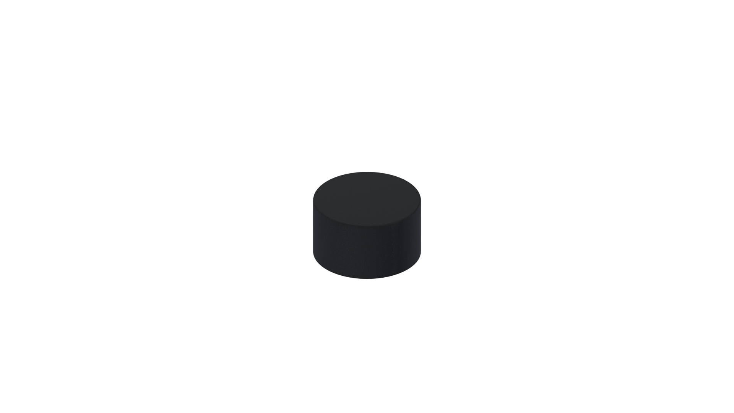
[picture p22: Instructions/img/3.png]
  

### 3. Reduce the height of the fan shroud

Saw the fan's stator in half in its shortest dimension. Make sure to not damage the stator electromagnets or any wires!

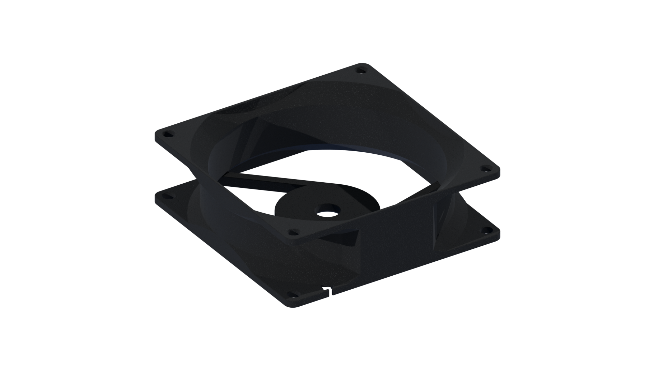
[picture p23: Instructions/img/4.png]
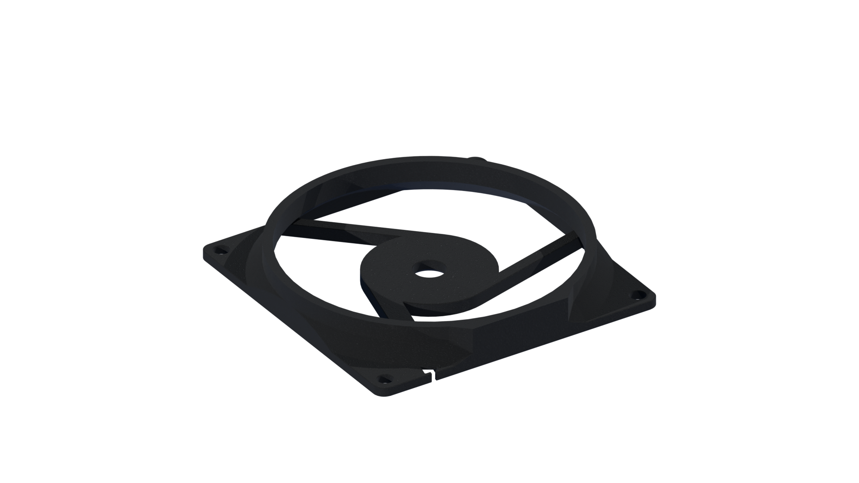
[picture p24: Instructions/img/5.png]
  

### 4. Install the skirt

Install the skirt onto the stator by simply pushing it into the shroud leftover. If the skirt is difficult to fit or is very loose after fitting, try rotating the skirt somewhat. If it still does not work properly, then feel free to either file away a bit of the skirt or use some glue to fix it to the stator, whichever is needed.

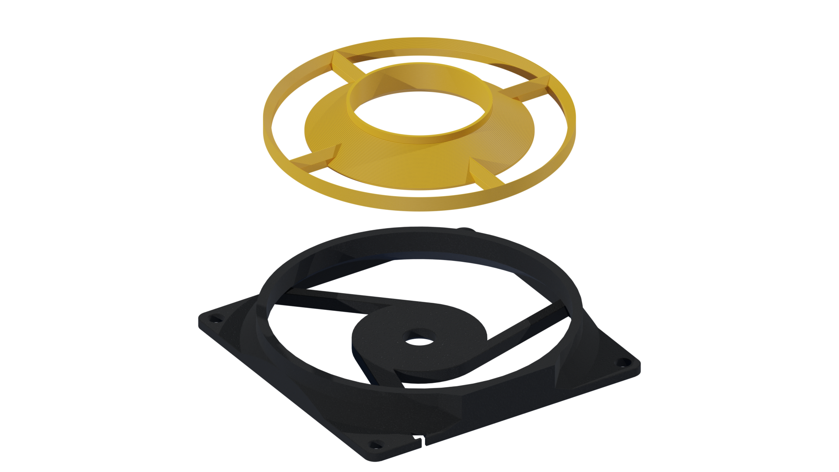
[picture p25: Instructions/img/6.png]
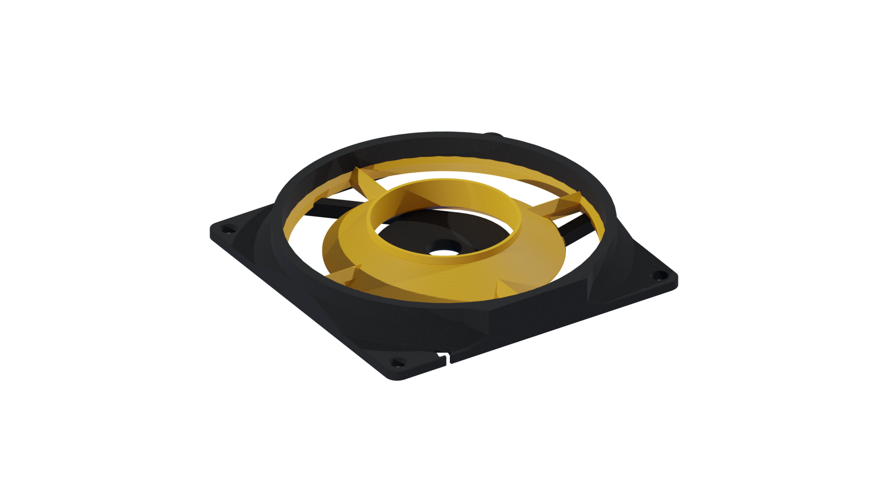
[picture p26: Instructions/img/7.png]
  

### 5. Install the hub

Install the hub onto the fan rotor by simply pushing it onto the rotor. The hub should not be able to easily move once fitted, but should still be possible to move without excessive force in order to be able to replace it if needed. You should not use glue to fix the hub onto the rotor. If the hub is too tight or too loose, then consider modifying the spin coater hub.FCStd or hub.stl file to fit your fan rotor's dimensions instead.

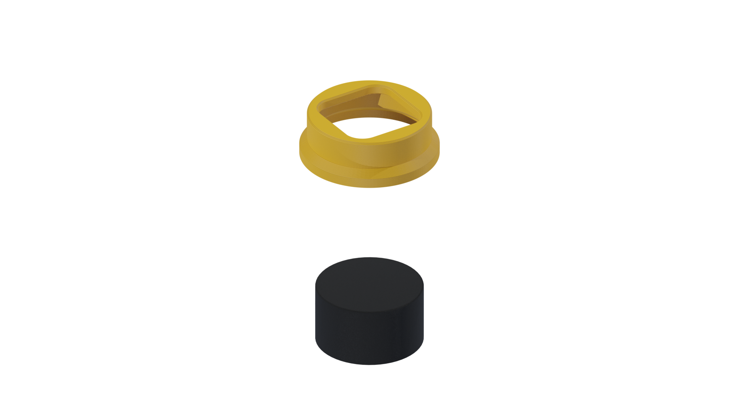
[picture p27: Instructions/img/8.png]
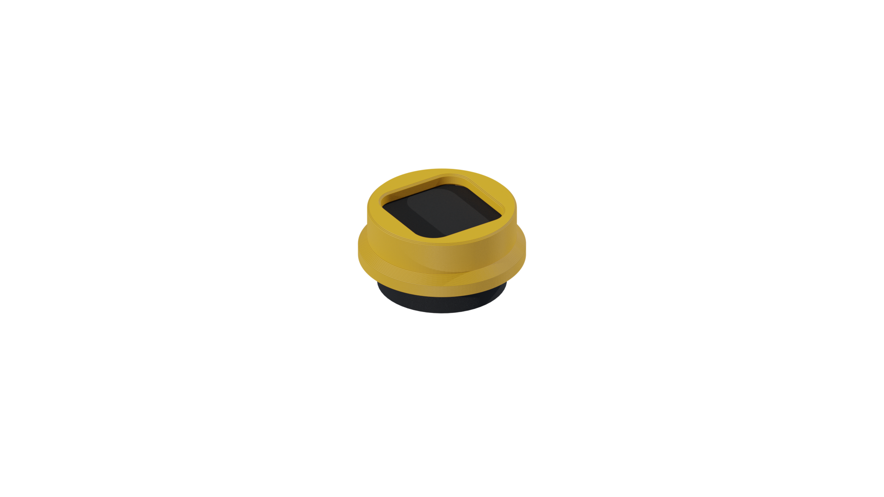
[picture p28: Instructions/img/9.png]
  

### 6. Reassemble the fan

Reassemble the rotor and stator of the fan. Make sure you put all ball bearings, washers, springs and other components of the fan that may have become loose during disassembly in their original positions. Make sure that the retaining ring at the bottom of the fan is properly in place.

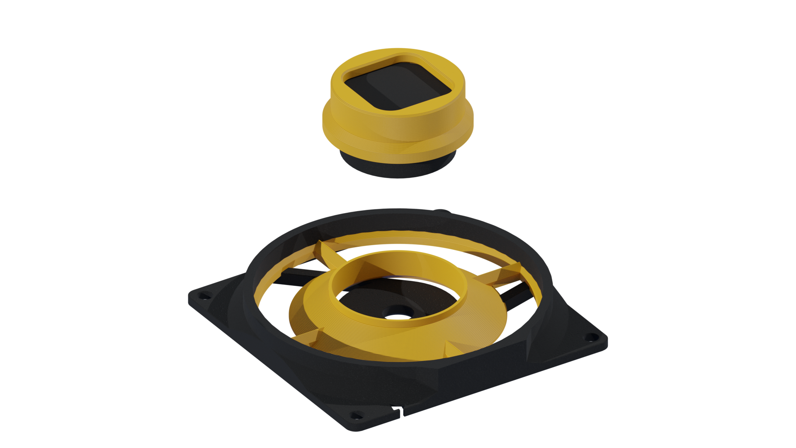
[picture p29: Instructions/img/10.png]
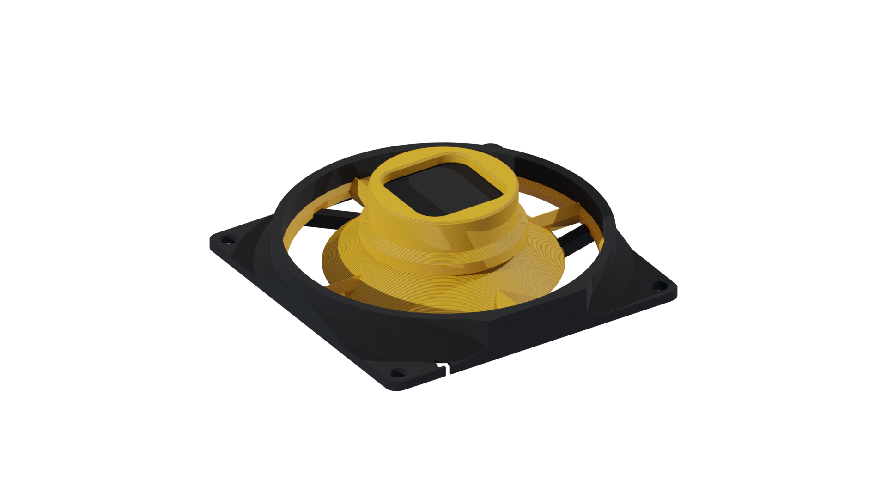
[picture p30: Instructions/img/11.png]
  

At this point, you have yourself a completed Spinner assembly

## 3. Assembly

Parts and tools needed

- 1x Chassis_0 part
- 1x Chassis_1 part
- 1x Chassis_2 part
- 1x Chassis_3 part
- Logic board
- Spinner assembly
- 1x Mount part
- 1x Spray catcher part
- 1x 16x2 LCD display module
- 1x 4x4 membrane matrix keypad
- 1x 15x21mm KCD1 power switch
- 1x Suitable DC-005 barrel jack
- 4x Anti-slip rubber furniture leg with M3 hole
- 1x 25x (empty) cd/dvd spindle
- 2x WH148 10K potentiometer
- 2x WH148 potentiometer knob
- 12x 3mm M3 heat set insert
- 4x 4mm M4 heat set insert
- 16x M3x10mm screw
- 4x M4x20mm or x17mm screw
- 2x 3mm round LED, different colors
- Preferred wires and connectors
- Screwdriver
- Soldering iron
- Drill with drill bits
- Hot glue gun or superglue

It's time to finally assemble the spin coater!

### 1. Make the spin chamber

Take the spindle case base and drill 4x 4mm holes in a square pattern around the center, each hole being 50.5mm from the center of the base. Then drill a large, 36-38mm diameter hole in the center of the base. You can also drill a medium sized hole (say about 15 to 20mm diameter) in the center of the see-through casing of the spindle case.

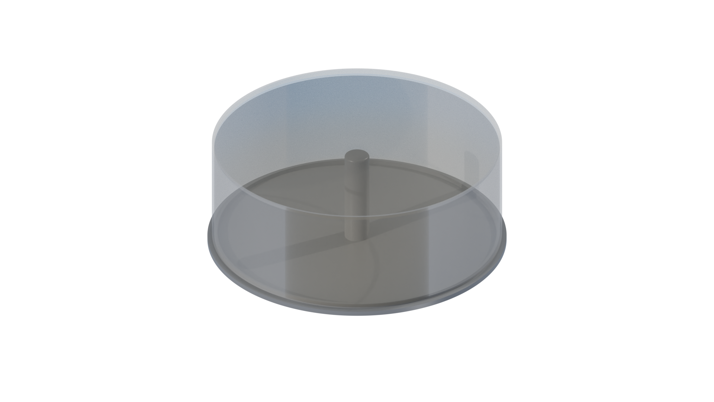
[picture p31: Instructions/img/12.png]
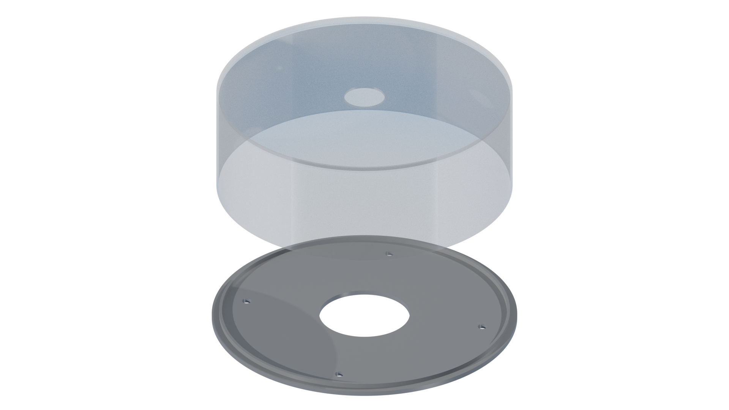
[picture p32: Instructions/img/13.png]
  

### 2. Install the logic board

Install the logic board into the Chassis_0 part. Use 4x M3x10mm screws to fix the board in place. The SD card slot should face towards the right of the board and line up with the hole in the chassis part.

Also install the power switch and the barrel jack power connector. The power switch fit might be too tight, in which case feel free to modify the switch to fit the corresponding hole better (or the chassis to accept the switch better). Use hot glue/superglue to fix the barrel jack to the chassis.

Connect up the power switch and connector to the logic board.

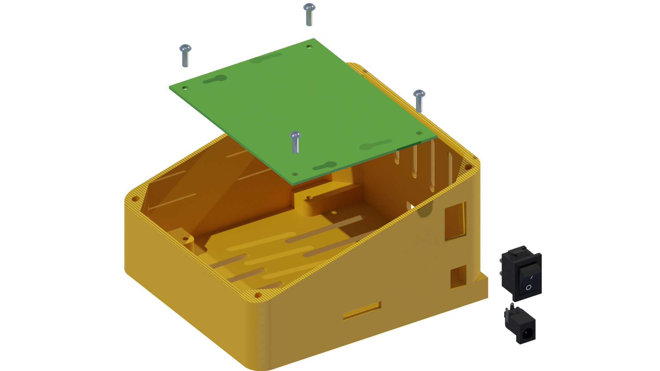
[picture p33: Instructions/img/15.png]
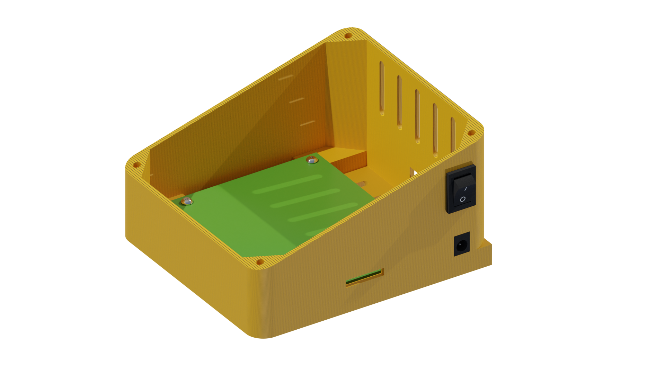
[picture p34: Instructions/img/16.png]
  

### 3. Add lid heat inserts

Use a soldering iron to add 4x M3 3mm heat set inserts into the 4 holes in the top slanted part of the chassis_0 part.

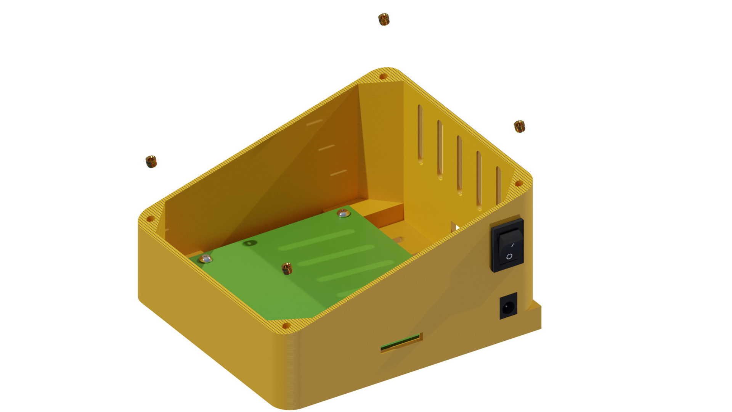
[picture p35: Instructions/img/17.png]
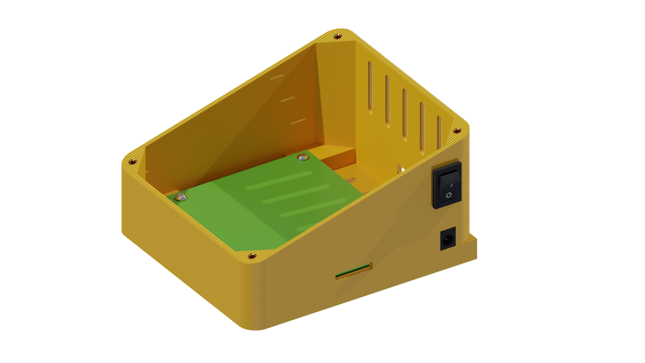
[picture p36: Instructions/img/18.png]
  

### 4. Install LCD and manual control potentiometers

Use hot glue/superglue to fix the 2x WH148 10K potentiometers to the chassis_2 part in their corresponding holes. Makes sure to leave enough room to connect wires to the potentiometers in order to connect them to the logic board later.

Use 4x M3x10mm screws to fix the LCD display to the chassis_2 part. If the display does not stay connected with the use of the screws only then also use 4x M3 nuts to keep the LCD display attached to the screws. The assembly graphics are somewhat incorrect!! The LCD should also attach to the underside (same side as the potentiometers) of the chassis_2 part!! This mistake persists throughout the manual! The author is terribly sorry for this.

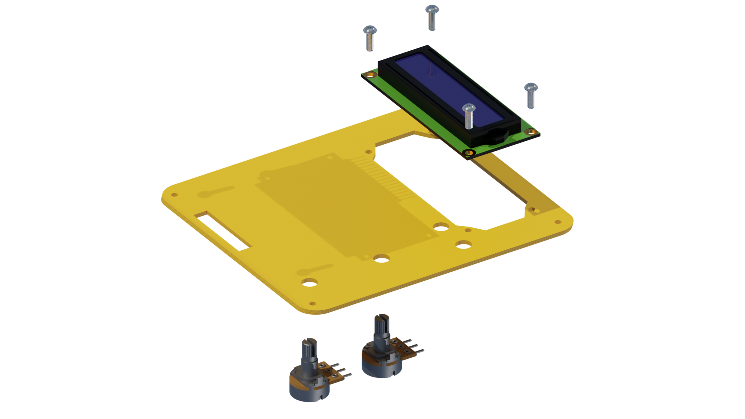
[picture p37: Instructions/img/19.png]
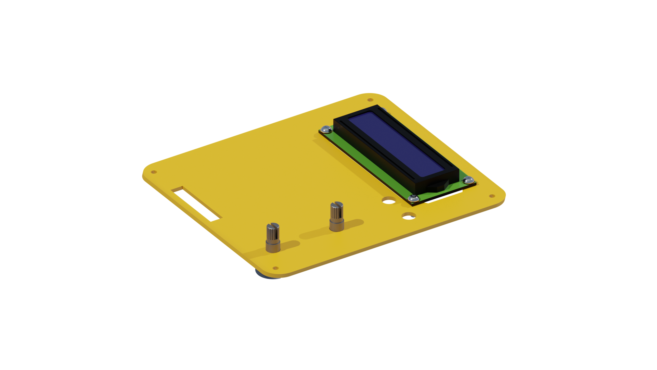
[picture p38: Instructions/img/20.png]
  

### 5. Install keypad and LED-s

If you chose to have the "power" indicator LED and "spinner active" LED, then use some hot glue or superglue to glue the 2x 3mm LED-s to the chassis_3 part in their corresponding holes.

Use some hot glue or superglue(preferred) to fix the 4x4 membrane matrix keypad to its corresponding slot in the chassis_3 part. Take note that the cable of the keypad should be facing downwards.

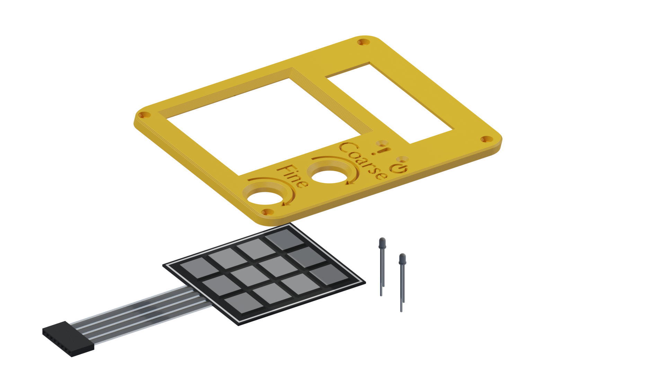
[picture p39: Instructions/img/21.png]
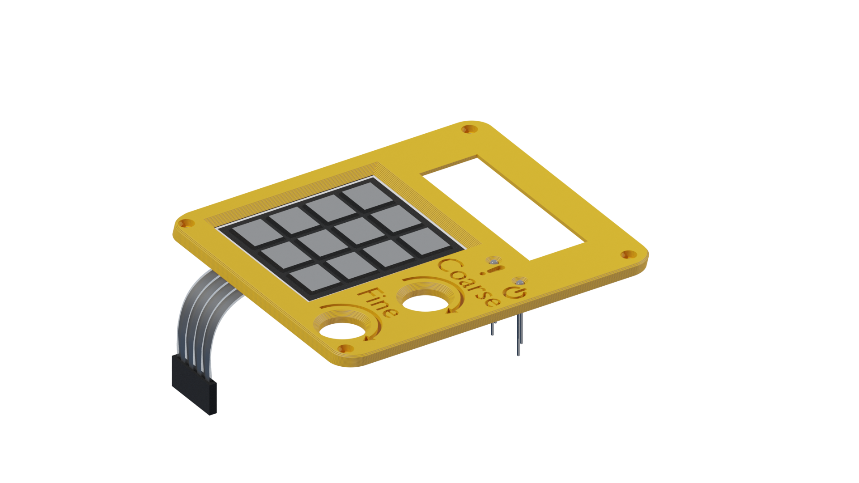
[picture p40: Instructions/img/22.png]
  

### 6. Assemble the Logic box

Take the populated chassis_0, chassis_2 and chassis_3 parts and sandwich them together, using 4x M3x10mm screws to keep them fixed together. Take note that the membrane matrix keypad cable should be routed through the hole in the bottom part of the chassis_2 part.

Don't forget to connect up any and all connections before fixing the chassis parts together! Take care to connect up all the connections correctly as messing with the connections at a later time is annoying...

Then take 2x WH148 potentiometer knobs and softly push them onto the exposed potentiometer ends.

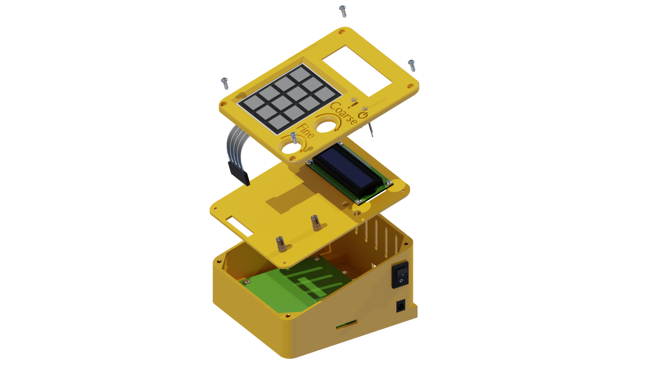
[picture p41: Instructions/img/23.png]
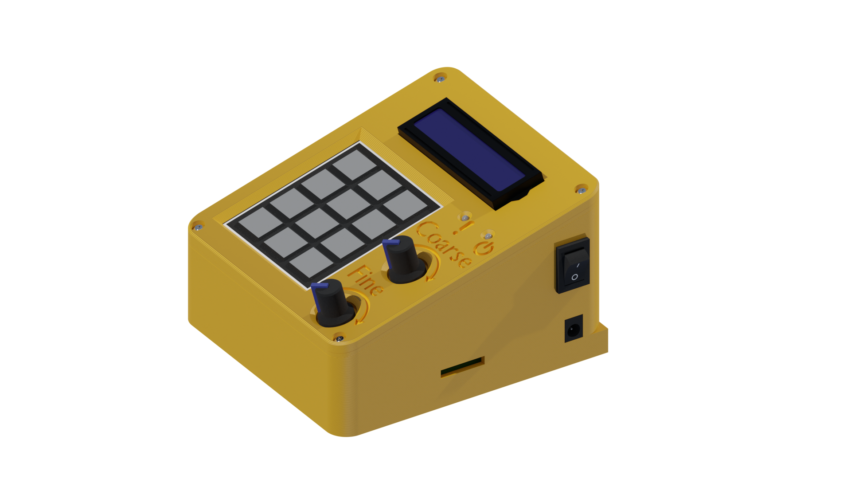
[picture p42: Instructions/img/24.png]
  

### 7. Connect up the spinner platform

Use a soldering iron to add 4x M3 3mm heat set inserts to the 4 holes at the back side of the assembled logic box. Then use 4x M3x10mm screws to gix the chassis_1 part to the logic box, giving you a spin coater assembly.

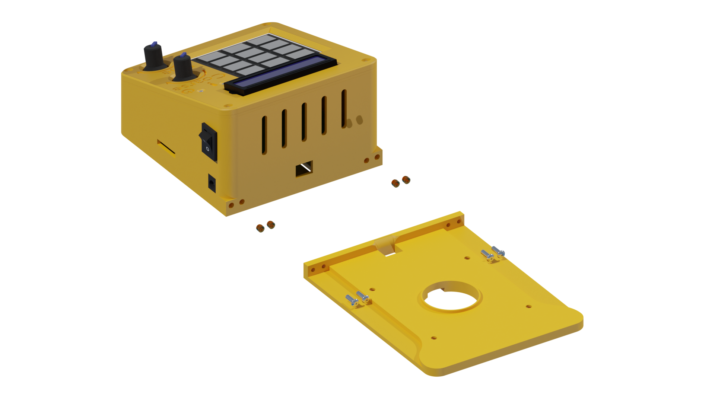
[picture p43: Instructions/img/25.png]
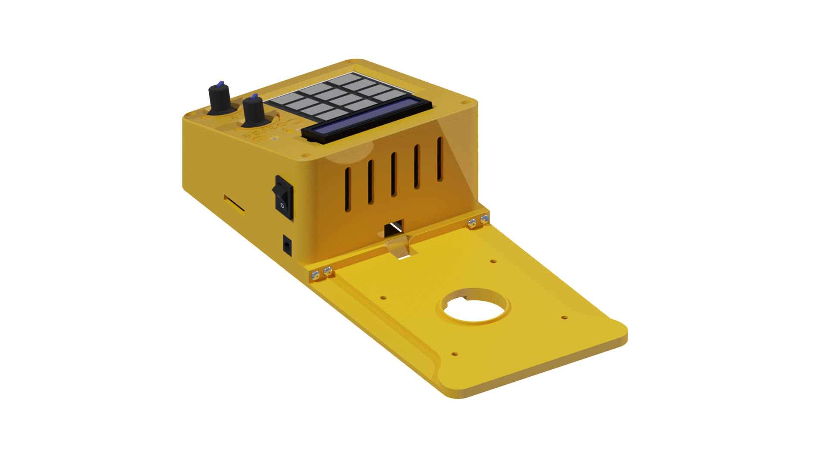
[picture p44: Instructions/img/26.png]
  

### 8. Install the remaining heat set inserts

Turn the spin coater over and use a soldering iron to install 4x M3 3mm heat set inserts, as well as 4x M4 4mm heat set inserts into their corresponding holes.

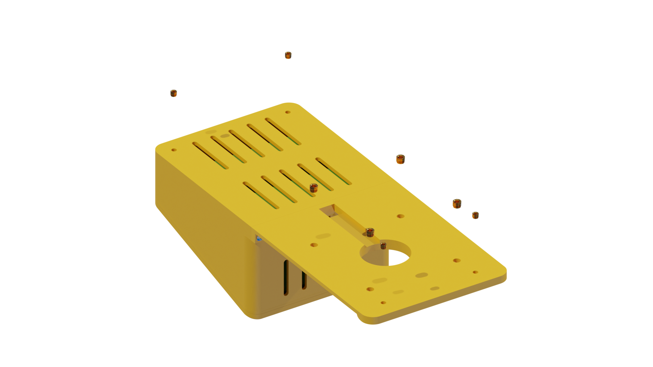
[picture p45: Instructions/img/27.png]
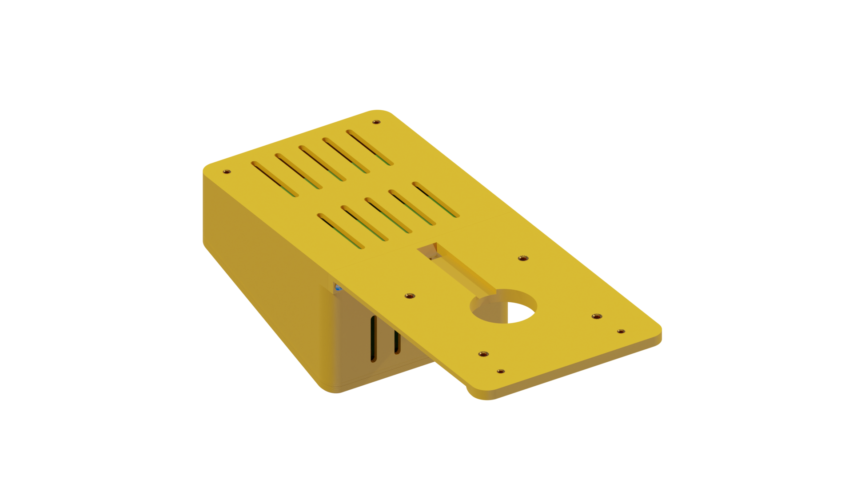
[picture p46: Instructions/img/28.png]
  

### 9. Add legs

Take 4x Anti-slip rubber furniture legs and fix them to the 4 corners by using 4x M3x10mm screws.

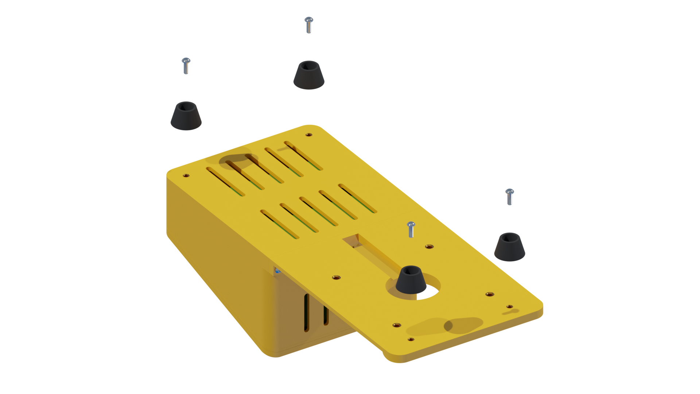
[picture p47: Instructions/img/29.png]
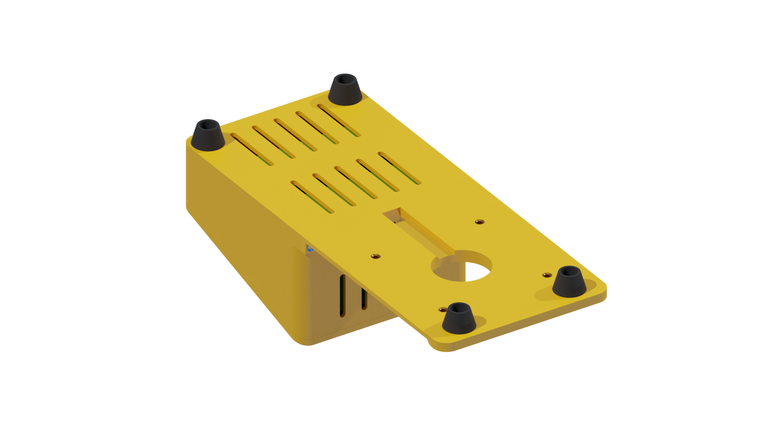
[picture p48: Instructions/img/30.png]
  

### Install the spinner assembly

Take thespinenr assembly, mount part as well as the modified cd spindle case base and sandwich them together. Use 4x M4x17mm or M4x20mm screws (17mm if not using the optional mount part) to fix them to the spin coater as shown below.

If the cd spindle case does not sit flush with the spinner platform, then feel free to add M4 nutes and/or washers as "standoffs".

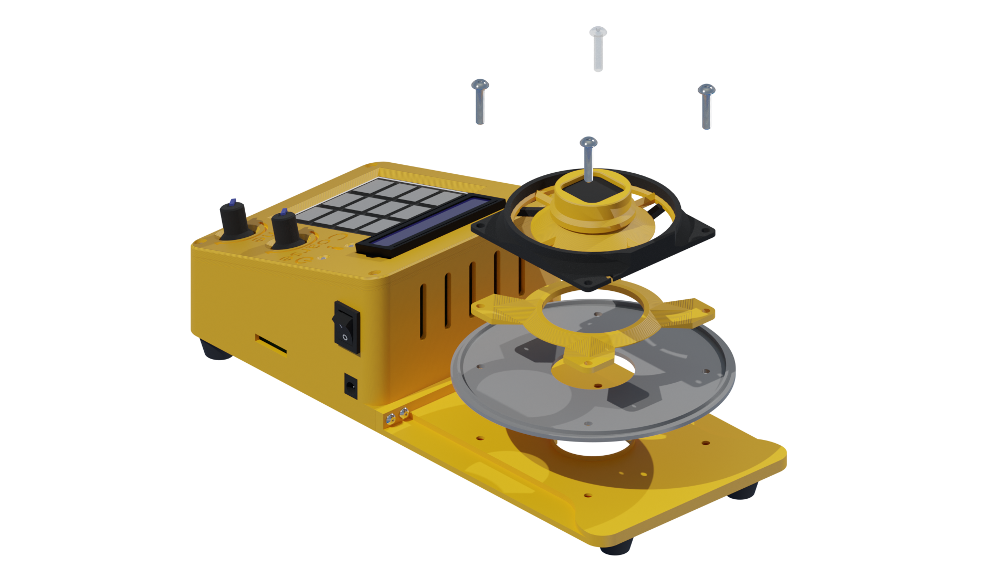
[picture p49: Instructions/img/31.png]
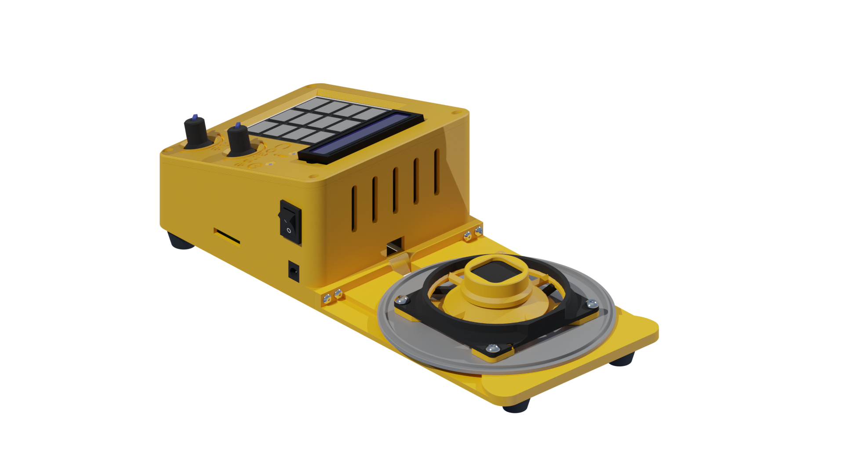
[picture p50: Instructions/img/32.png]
  

### 10.* Finish the spin chamber

If you opted to also make a spray catcher part(recommended) then it should be possible to simply slip it onto the spin coater as shown. The cd spindle case cover should be able to fit over this spray catcher and still be able to lock onto the cd spindle case base.

When using the spin coater, it is always recommended to have both the spray catcher and the cover installed during spinning in order to reduce the chance that any of your coating liquid sprays out of the chamber. In addition it prevents any of the spray from getting through the ventilation holes at the back of the logic box of the spin coater and potentially shorting the electronics.

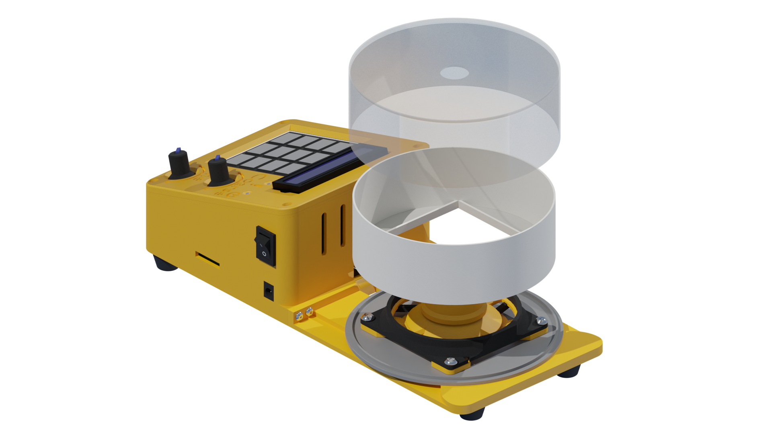
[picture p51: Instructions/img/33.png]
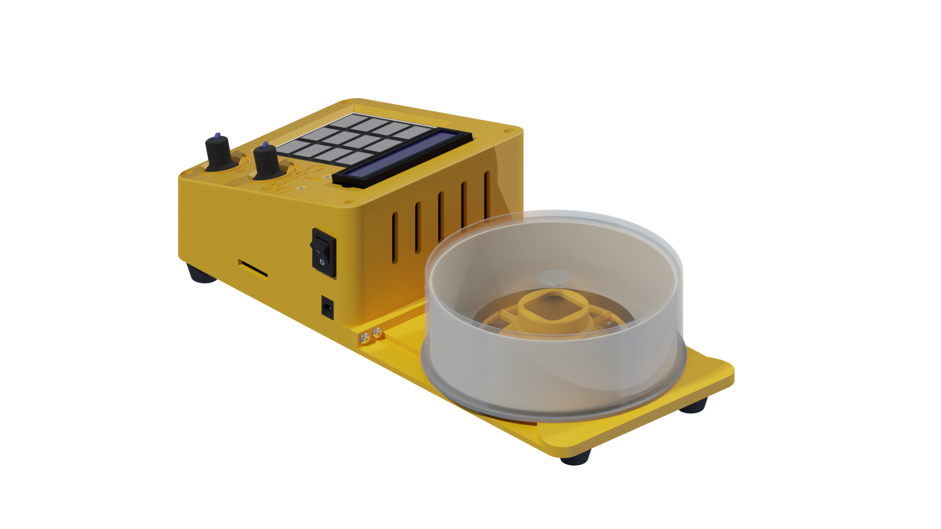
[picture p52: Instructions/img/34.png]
  

# All Done! Enjoy!



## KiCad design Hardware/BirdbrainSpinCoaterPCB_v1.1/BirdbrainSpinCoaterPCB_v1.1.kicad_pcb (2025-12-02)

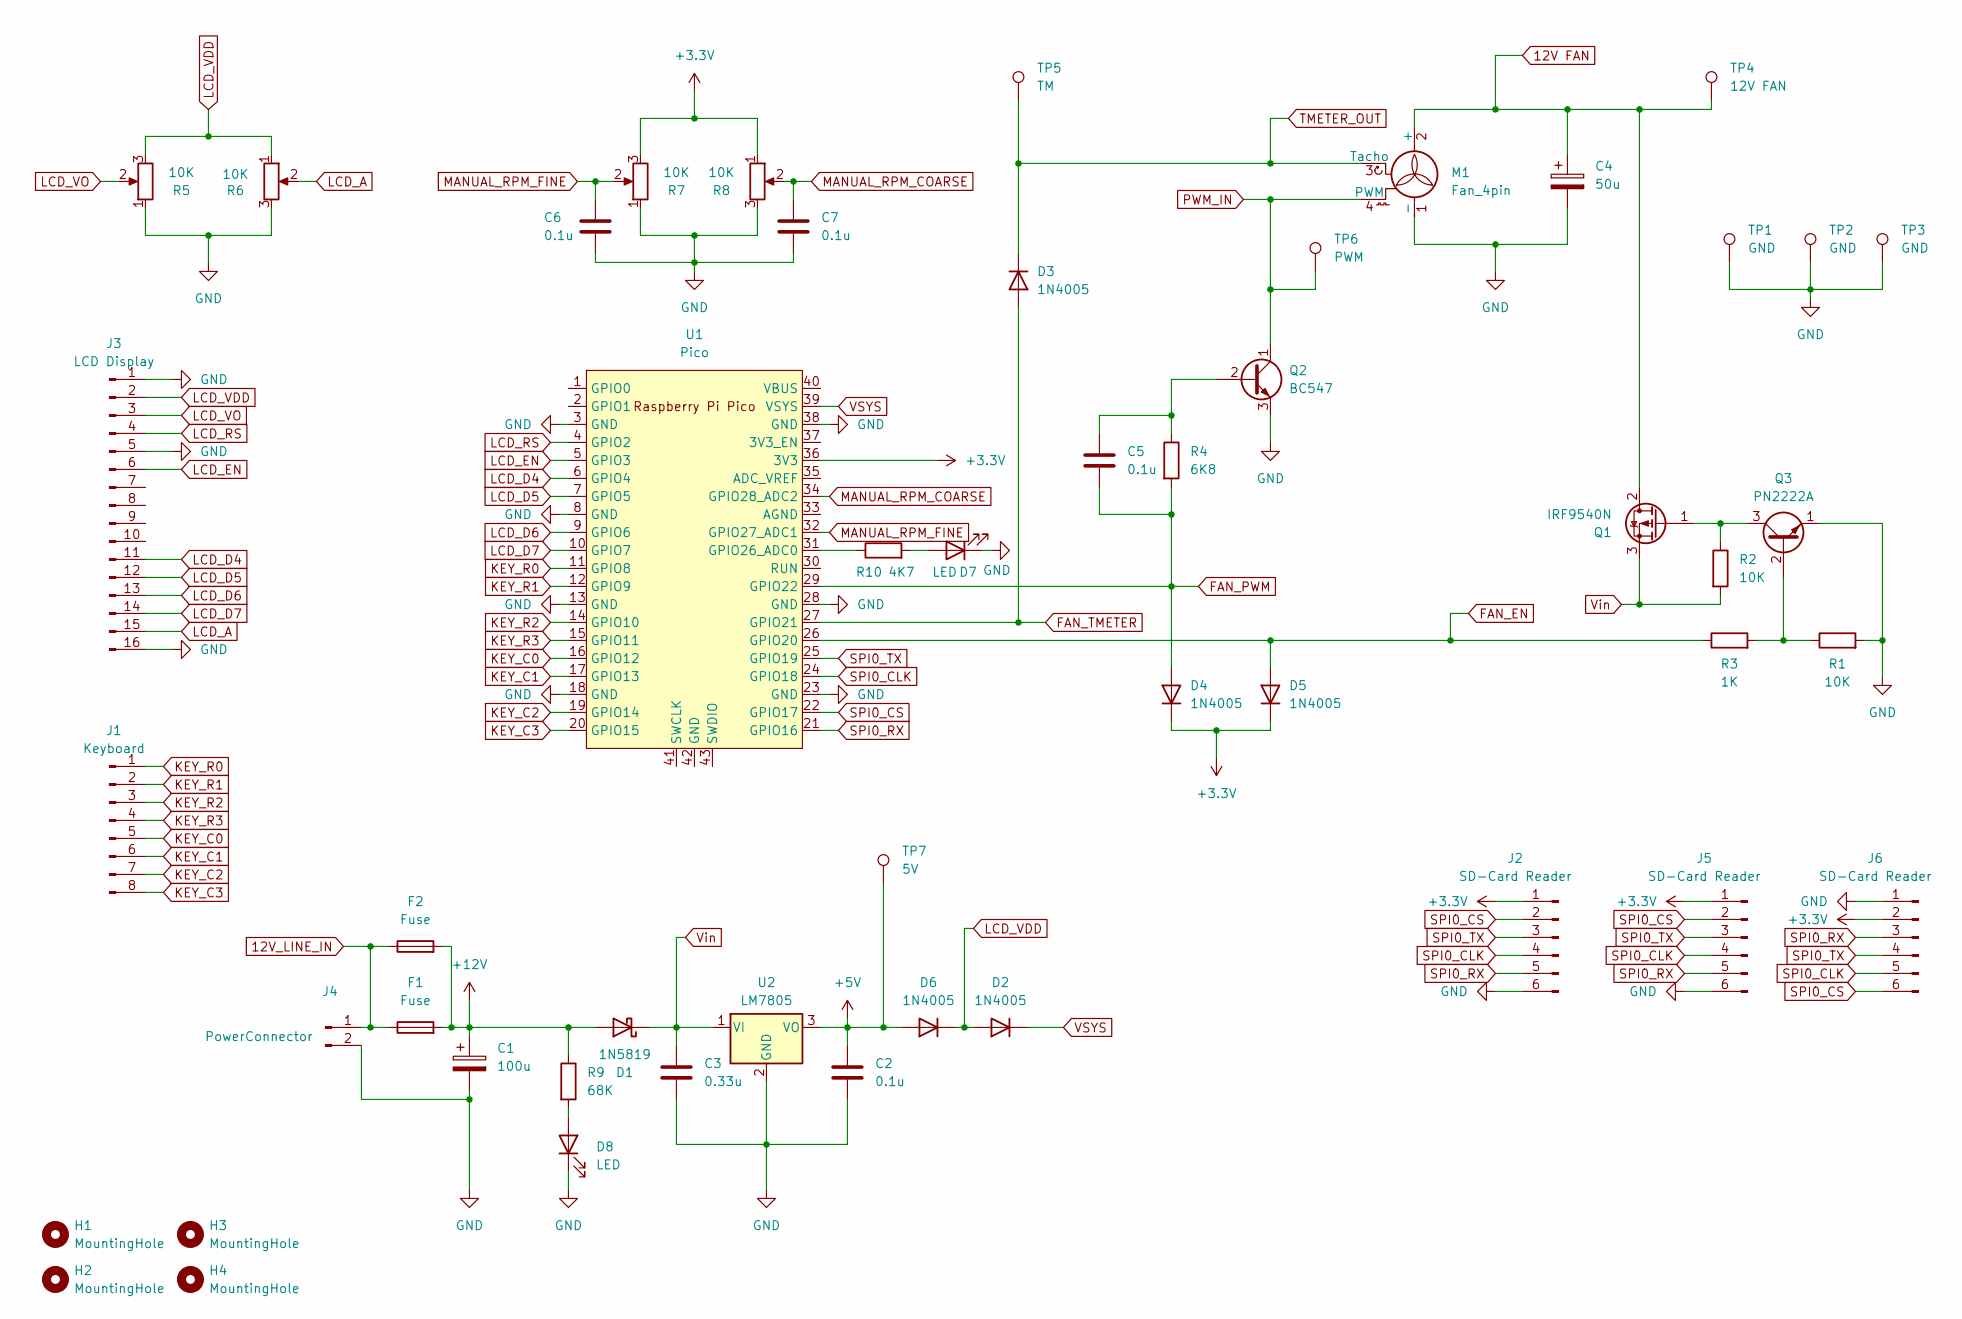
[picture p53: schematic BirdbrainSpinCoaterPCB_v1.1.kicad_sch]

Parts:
C1: 100u; CP_Radial_D5.0mm_P2.00mm
C2, C5, C6, C7: 0.1u; DualFootprint_C1206_Radial
C3: 0.33u; DualFootprint_C1206_Radial
C4: 50u; CP_Radial_D5.0mm_P2.00mm
D1: 1N5819; D_DO-41_SOD81_SOD123_P10.16mm_Horizontal
D2, D3, D4, D5, D6: 1N4005; D_DO-41_SOD81_SOD123_P10.16mm_Horizontal
D7, D8: LED; LED_D5.0mm
F1: Fuse; Fuseholder_Clip-5x20mm_Littelfuse_100_Inline_P20.50x4.60mm_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
F2: Fuse; Fuse_1210_3225Metric
H1, H2, H3, H4: MountingHole; MountingHole_3.2mm_M3
J1: Keyboard; PinHeader_1x08_P2.54mm_Vertical
J2, J5, J6: SD-Card Reader; PinHeader_1x06_P2.54mm_Vertical
J3: LCD Display; PinHeader_1x16_P2.54mm_Vertical
J4: PowerConnector; TerminalBlock_Phoenix_MKDS-1,5-2-5.08_1x02_P5.08mm_Horizont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
M1: Fan_4pin; PinHeader_1x04_P2.54mm_Vertical
Q1: IRF9540N; TO-220-3_Vertical
Q2: BC547; TO-92_Dual
Q3: PN2222A; TO-92_Dual
R1, R2: 10K; DualFootprint_R1206_Axial7.62
R3: 1K; DualFootprint_R1206_Axial7.62
R4: 6K8; DualFootprint_R1206_Axial7.62
R5, R6, R7, R8: 10K; Potentiometer_Bourns_3296W_Vertical
R9: 68K; DualFootprint_R1206_Axial7.62
R10: 4K7; DualFootprint_R1206_Axial7.62
TP1, TP2, TP3: GND; PinHeader_1x01_P2.54mm_Vertical
TP4: 12V FAN; PinHeader_1x01_P2.54mm_Vertical
TP5: TM; PinHeader_1x01_P2.54mm_Vertical
TP6: PWM; PinHeader_1x01_P2.54mm_Vertical
TP7: 5V; PinHeader_1x01_P2.54mm_Vertical
U1: Pico; RPi_Pico_SMD_TH
U2: LM7805; TO-220-3_Vertical

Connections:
12V FAN: C4.1, M1.2 (+), Q1.2 (D), TP4.1
12V_LINE_IN: F1.1, F2.1, J4.1
+3.3V: D4.1 (K), D5.1 (K), J2.1, J5.1, J6.2, R7.3, R8.1, U1.36 (3V3)
+5V: C2.1, D6.2 (A), TP7.1, U2.3 (VO)
+12V: C1.1, D1.2 (A), F1.2, F2.2, R9.1
FAN_EN: D5.2 (A), R3.1, U1.26 (GPIO20)
FAN_PWM: C5.2, D4.2 (A), R4.2, U1.29 (GPIO22)
FAN_TMETER: D3.2 (A), U1.27 (GPIO21)
GND: C1.2, C2.2, C3.2, C4.2, C6.2, C7.2, D7.1 (K), D8.1 (K), J2.6, J3.1, J3.5, J3.16, J4.2, J5.6, J6.1, M1.1 (-), Q2.3 (E), Q3.1 (E), R1.2, R5.1, R6.3, R7.1, R8.3, TP1.1, TP2.1, TP3.1, U1.3 (GND), U1.8 (GND), U1.13 (GND), U1.18 (GND), U1.23 (GND), U1.28 (GND), U1.38 (GND), U2.2 (GND)
KEY_C0: J1.5, U1.16 (GPIO12)
KEY_C1: J1.6, U1.17 (GPIO13)
KEY_C2: J1.7, U1.19 (GPIO14)
KEY_C3: J1.8, U1.20 (GPIO15)
KEY_R0: J1.1, U1.11 (GPIO8)
KEY_R1: J1.2, U1.12 (GPIO9)
KEY_R2: J1.3, U1.14 (GPIO10)
KEY_R3: J1.4, U1.15 (GPIO11)
LCD_A: J3.15, R6.2
LCD_D4: J3.11, U1.6 (GPIO4)
LCD_D5: J3.12, U1.7 (GPIO5)
LCD_D6: J3.13, U1.9 (GPIO6)
LCD_D7: J3.14, U1.10 (GPIO7)
LCD_EN: J3.6, U1.5 (GPIO3)
LCD_RS: J3.4, U1.4 (GPIO2)
LCD_VDD: D2.2 (A), D6.1 (K), J3.2, R5.3, R6.1
LCD_VO: J3.3, R5.2
MANUAL_RPM_COARSE: C7.1, R8.2, U1.34 (GPIO28_ADC2)
MANUAL_RPM_FINE: C6.1, R7.2, U1.32 (GPIO27_ADC1)
unnamed: D7.2 (A), R10.2
unnamed: D8.2 (A), R9.2
unnamed: Q1.1 (G), Q3.3 (C), R2.1
unnamed: C5.1, Q2.2 (B), R4.1
unnamed: Q3.2 (B), R1.1, R3.2
unnamed: R10.1, U1.31 (GPIO26_ADC0)
PWM_IN: M1.4 (PWM), Q2.1 (C), TP6.1
SPI0_CLK: J2.4, J5.4, J6.5, U1.24 (GPIO18)
SPI0_CS: J2.2, J5.2, J6.6, U1.22 (GPIO17)
SPI0_RX: J2.5, J5.5, J6.3, U1.21 (GPIO16)
SPI0_TX: J2.3, J5.3, J6.4, U1.25 (GPIO19)
TMETER_OUT: D3.1 (K), M1.3 (Tacho), TP5.1
VSYS: D2.1 (K), U1.39 (VSYS)
Vin: C3.1, D1.1 (K), Q1.3 (S), R2.2, U2.1 (VI)

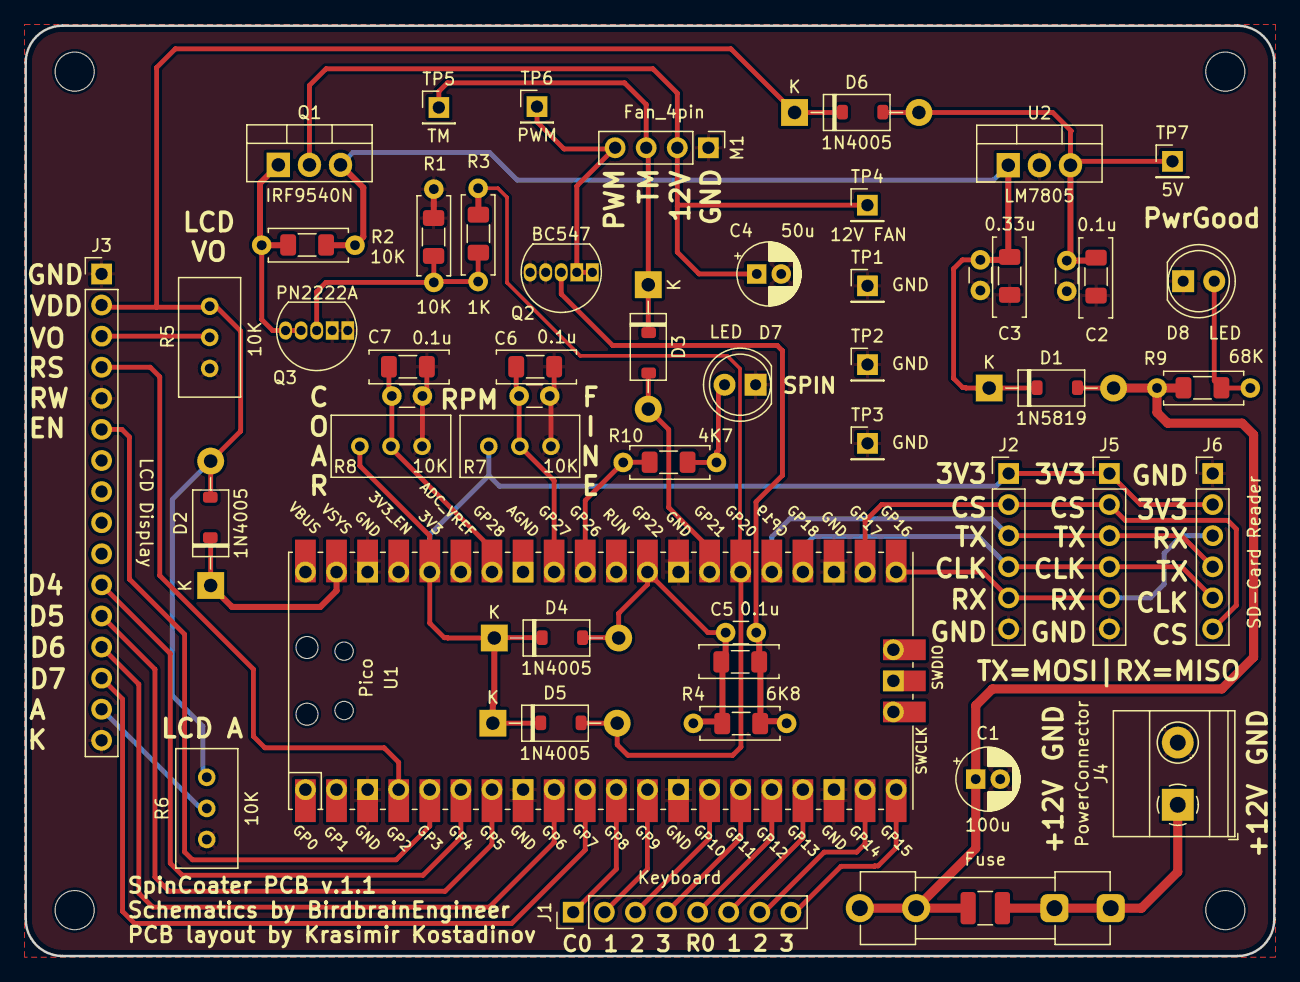
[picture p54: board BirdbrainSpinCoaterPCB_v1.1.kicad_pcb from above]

Board: 2 copper layers, 102.0 x 76.0 mm, 50 parts (0 on the bottom side), 42 nets.

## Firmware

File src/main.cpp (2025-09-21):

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
#include <main.h>

#define HW_REVISION 2
#define DEBUG false //Enables serial over usb

// ============================GPIO PINOUT==================================
// Make sure to set the pinout for your implementation! Do not change the pin variable names!
// 0 used for usb, I think
// 1 used for usb, I think...?
const int lcd_rs = 2;
const int lcd_en = 3;
#if HW_REVISION == 1
const int lcd_d4 = 5;
const int lcd_d5 = 4;
#else
const int lcd_d4 = 4; 
const int lcd_d5 = 5;
#endif
const int lcd_d6 = 6;
const int lcd_d7 = 7;
const int membrane_row_0_pin = 8;
const int membrane_row_1_pin = 9;
const int membrane_row_2_pin = 10;
const int membrane_row_3_pin = 11;
const int membrane_col_0_pin = 12;
const int membrane_col_1_pin = 13;
const int membrane_col_2_pin = 14;
const int membrane_col_3_pin = 15;
//=====================
const int SPI0_RX = 16;  //Do not change! Arduino-pico core default pin, used for SD card reader
const int SPI0_SC = 17;  //Do not change! Arduino-pico core default pin, used for SD card reader
const int SPI0_CLK = 18; //Do not change! Arduino-pico core default pin, used for SD card reader
const int SPI0_TX = 19;  //Do not change! Arduino-pico core default pin, used for SD card reader
const int spinner_power_enable_pin = 20;
const int tachometer_pin = 21;
const int motor_pwm_pin = 22;
// pin 23 not available
// pin 24 not available
// pin 25 not available
const int spinner_running_led_pin = 26;
const int manual_rpm_fine_adjust_pin = 27; //Must be an analog pin
const int manual_rpm_coarse_adjust_pin = 28; //Must be an analog pin


// ========================Program constants================================
const float motorPWMFrequency = 25000.0;
const long tachometerDebounceInterval = 10; //if microseconds, increase if double presses happen regularly. 
const u8_t keypadRows = 4; //Not recommended to change the membrane keypad size to be different from 4x4.
const u8_t keypadCols = 4; //Not recommended to change the membrane keypad size to be different from 4x4.
const char keys[keypadRows][keypadCols] = { //if your keypad has a different key layout, then it can be changed here.
  {'1','2','3','A'},
  {'4','5','6','B'},
  {'7','8','9','C'},
  {'*','0','#','D'}
};
char ENTER = '#';
char BACK = '*';
char UP = 'C';
char DOWN = 'D';
char YES = 'A';
char NO = 'B';
char DOT = 'D';
const Config defaultConfig = { //Default configuration for first boot and/or if SD card memory is not found.
  .Kp = 0.18, 
  .Ki = 0.09, 
  .Kd = 0.0025, 
  .analogAlpha = 0.01, //This shouldn't be changed unless you really know what's going on.
  .rpmAlpha = 0.2, //This shouldn't be changed unless you really know what's going on.
  .minDutyCycle = 10.0 //Some fans may need a higher minimum duty cycle. It is recommended to update it through spinner menu.
};
const int analogInterruptInterval = 100; //Should not be necessary to change.
const float controllerMinOutput = 12.0; //default
const float controllerMaxOutput = 100.0; //default
const u16_t inputBufferSize = 16; //It is highly recommended to not change this.
uint8_t backslash[8] = {
  0b00000,
  0b10000,
  0b01000,
  0b00100,
  0b00010,
  0b00001,
  0b00000
};
uint8_t rightArrow[8] = {
  0b00000,
  0b00100,
  0b00010,
  0b11111,
  0b00010,
  0b00100,
  0b00000
};
uint8_t deltaSign[8] = {
  0b00000,
  0b00000,
  0b00100,
  0b01010,
  0b10001,
  0b11111,
  0b00000
};
const u8_t rowPins[keypadRows] = {membrane_row_0_pin, membrane_row_1_pin, membrane_row_2_pin, membrane_row_3_pin};
const u8_t colPins[keypadCols] = {membrane_col_0_pin, membrane_col_1_pin, membrane_col_2_pin, membrane_col_3_pin};
const unsigned int keypadDebounceInterval = 100;
const unsigned long coreLoopInterval = 500; //in micros
volatile float analogAlpha = config.analogAlpha;
volatile float rpmAlpha = config.rpmAlpha;
const char jobsPath[] = "/jobs/";
const char jobsFolderPath[] = "/jobs";
const char configFilePath[] = "/config";
const u8_t maxFileNameLength = 16;
const u8_t maxJobNameLength = 9;


// =========================Inter-Core variables==============================
volatile float analogDutyCycle = 0.0;
volatile bool pidEnabled = false;
volatile float rpmTarget = 0.0;
volatile float currentRPM = 0.0;
volatile float pidDutyCycle = 0.0;
volatile Config config = {
  .Kp = defaultConfig.Kp,
  .Ki = defaultConfig.Ki,
  .Kd = defaultConfig.Kd,
  .analogAlpha = defaultConfig.analogAlpha,
  .rpmAlpha = defaultConfig.rpmAlpha,
  .minDutyCycle = defaultConfig.minDutyCycle
};
volatile Config storedConfig = {0.0, 0.0, 0.0, 0.0, 0.0, 0.0};
volatile bool motorEnabled = false;
volatile float minDutyCycle = config.minDutyCycle;
RP2040_PWM* motorDriver;
PID_controller* pidController;


// ========================Core-specific variables===========================

//@@@@@@@@@@@@@@@@@@@@@@@@@@@@@@@  Core-0  @@@@@@@@@@@@@@@@@@@@@@@@@@@@@@@@@@@
File myFile;
LiquidCrystal lcd = LiquidCrystal(lcd_rs, lcd_en, lcd_d4, lcd_d5, lcd_d6, lcd_d7);
BBkeypad* keypad;
MenuController* menuController;
JobTable* jobTable;
bool cursorBlinker = false;
unsigned long inputBufferIndex = 0;
bool memoryGood = true;
bool pidTestAvailable = false;
bool quickRunJobAvailable = false;
SpinnerJob* pidTestJob = nullptr;
SpinnerJob* quickRunJob = nullptr;


//@@@@@@@@@@@@@@@@@@@@@@@@@@@@@@@  Core-1  @@@@@@@@@@@@@@@@@@@@@@@@@@@@@@@@@@@

RPI_PICO_Timer ITimer3(3);
SWtimer* coreLoop;
unsigned long core1Timer = 0;
unsigned long core1Loops = 0;

// =======================Interrupt variables=================================
volatile unsigned long rpmTimer = 0;
volatile float analogAverage = 0.01;
volatile unsigned long microsSinceLastRpmCount = 0;
volatile bool newRpmData = false;


// ===========================CODE======================================

//@@@@@@@@@@@@@@@@@@@@@@@@@@@@@@@  Core-0  @@@@@@@@@@@@@@@@@@@@@@@@@@@@@@@@@@@
void setup() {
  if(DEBUG){
    while(!Serial); // Wait for Serial to be ready
    {
      delay(11);
    }
    Serial.println("Core 0 starting.");
  }
  lcd.begin(16, 2);
  lcd.print("Initializing...");
  lcd.setCursor(0, 1);
  lcd.print("Init keypad...   ");

  keypad = new BBkeypad((char*)keys, keypadCols, keypadRows, colPins, rowPins);
  lcd.createChar(1, backslash);
  lcd.createChar(2, rightArrow);
  lcd.createChar(3, deltaSign);

  lcd.setCursor(0, 1);
  lcd.print("Init memory...   ");
  if (!SD.begin(17)) {
    printlcdErrorMsg("SD card not\nfound!");
    memoryGood = false;
    printlcdErrorMsg(" Functionality\nhighly limited!");
    config.Kd = defaultConfig.Kd;
    config.Ki = defaultConfig.Ki;
    config.Kp = defaultConfig.Kp;
    config.analogAlpha = defaultConfig.analogAlpha;
    config.rpmAlpha = defaultConfig.rpmAlpha;
    config.minDutyCycle = defaultConfig.minDutyCycle;
  }
  else {
    // Checks whether Jobs directory exists, if not, creates it. If a file with the same name exists, deletes it
    if(SD.exists(jobsFolderPath)){
      myFile = SD.open(jobsFolderPath);
      if(myFile.isDirectory()){
        myFile.close();
      }
      else{
        myFile.close();
        SD.remove(jobsFolderPath);
        SD.mkdir(jobsFolderPath);
      }
    }
    else{
      SD.mkdir(jobsFolderPath);
    }
    loadConfiguration(config);
  }

  lcd.setCursor(0, 1);
  lcd.print("Init menu...     ");
  menuController = new MenuController(mainMenuConstructor, printlcdErrorMsg);
  menuController->init(10, reboot);
  if(memoryGood){
    lcd.setCursor(0, 1);
    lcd.print("Init jobs...     ");
    jobTable = new JobTable(jobsFolderPath);
    auto jobsDirectory = SD.open(jobsFolderPath);
    while(auto jobFile = jobsDirectory.openNextFile()){
      SpinnerJob* job = loadJob(jobFile);
      if(job == nullptr){ printlcdErrorMsg("Error loading\na job file!"); }
      else{
        if(!jobTable->addJob(job)){ 
          printlcdErrorMsg("Too many jobs\nsaved to memory!"); 
          break;
        }
      }
      jobFile.close();
    }
    jobsDirectory.close();
    auto defaultJobFile = SD.open("/pid");
    if(!defaultJobFile){
      pidTestAvailable = false;
      printlcdErrorMsg("Missing PID\ntest job file!");
    }
    else {
      pidTestJob = loadJob(defaultJobFile);
      if(pidTestJob == nullptr){
        printlcdErrorMsg("PID test job\nfile corrupted!");
        pidTestAvailable = false;
      }
      else{ pidTestAvailable = true; }
    }
    defaultJobFile.close();
  }
  pidController = new PID_controller(config.Kp, config.Ki, config.Kd, config.minDutyCycle, 100.0);
  if(DEBUG) {Serial.println("Core 0 started.");}
}

void loop() {
  lcd.clear();
  MenuControlSignal menuSignal = IDLE;
  MenuContext menuContext = menuController->update(menuSignal);
  renderMenuContext(menuContext);
  char key;
  while(true){
    if(keypad->pollState(KeyState::KEY_DOWN) != 0){
      key = keypad->buffer[0].key;
      if(key == ENTER){ menuSignal = SELECT; }
      else if(key == BACK){ menuSignal = RETRACT; }
      else if(key == UP){ menuSignal = PREVITEM; }
      else if(key == DOWN){ menuSignal = NEXTITEM; }
      else{ menuSignal = IDLE; }
      menuContext = menuController->update(menuSignal);
      renderMenuContext(menuContext);
    }
    delay(10);
  }
}


//@@@@@@@@@@@@@@@@@@@@@@@@@@@@@@@  Core-1  @@@@@@@@@@@@@@@@@@@@@@@@@@@@@@@@@@@
void setup1() {
  if(DEBUG){
    while(!Serial); // Wait for Serial to be ready
    {
      delay(9);
    }
    Serial.println("Core 1 starting.");
  }
  motorDriver = new RP2040_PWM(motor_pwm_pin, motorPWMFrequency, 0.0);
  coreLoop = new SWtimer(coreLoopInterval, true);

  pinMode(spinner_power_enable_pin, OUTPUT);
  pinMode(spinner_running_led_pin, OUTPUT);
  pinMode(tachometer_pin, INPUT_PULLUP);

  disableMotor();

  attachInterrupt(tachometer_pin, tachInterrupt, CHANGE);
  rpmTimer = micros();

  pinMode(manual_rpm_coarse_adjust_pin, INPUT);
  pinMode(manual_rpm_fine_adjust_pin, INPUT);
  analogReadResolution(16);
  ITimer3.attachInterruptInterval(analogInterruptInterval, analogInterrupt);
  core1Timer = micros();
  interrupts();
  coreLoop->start();
  if(DEBUG) {Serial.println("Core 1 setup complete.");}
}

void loop1() {
  while(true){
    if(coreLoop->poll()){
      if(motorEnabled){
        float currentDutyCycle;
        if(pidEnabled){
          currentDutyCycle = 100.0 - pidController->compute(rpmTarget, currentRPM, coreLoopInterval);
        }
        else{
          currentDutyCycle = analogDutyCycle;
        }
        motorDriver->setPWM(motor_pwm_pin, motorPWMFrequency, currentDutyCycle);
      }
    }
  }
}


// @@@@@@@@@@@@@@@@@@@@@@@@@  Interrupts  @@@@@@@@@@@@@@@@@@@@@@@@@@@@@@@@@@@@@

void tachInterrupt(){
  unsigned long currentTime = micros();
  unsigned long microsElapsed = currentTime - rpmTimer;
  if (microsElapsed < tachometerDebounceInterval) { return; }
  microsSinceLastRpmCount = microsElapsed;
  //Serial.printf("1000000 / %f * 15 = %f\n", (float)microsElapsed, 1000000.0 / (double)(microsElapsed) * 15.0);
  double rpmSample = 1000000.0 / (double)(microsElapsed) * 15.0; // 15.0 is for four transitions per revolution (rps * 60 / 4)
  currentRPM = (float)((rpmSample * (double)rpmAlpha) + ((double)currentRPM * (1.0 - (double)rpmAlpha)));
  rpmTimer = currentTime;
  //Serial.printf("RPM: %f, Micros: %lu RPM Sample: %f\n", currentRPM, microsElapsed, (float)rpmSample);
}

bool analogInterrupt(struct repeating_timer *t){
  // Exponential moving average
  int reading = (analogRead(manual_rpm_coarse_adjust_pin) + analogRead(manual_rpm_fine_adjust_pin) / 10);
  reading = reading > 65535 ? 65535 : (reading < 0 ? 0 : reading);
  float analogNewAverage = ((float)(reading) * analogAlpha) + (analogAverage * (1.0 - analogAlpha));
  analogAverage = analogNewAverage;
  analogDutyCycle = analogNewAverage * 0.0015259;
  return true;
}

// @@@@@@@@@@@@@@@@@@@@@@@@@  Functions @@@@@@@@@@@@@@@@@@@@@@@@@@@@@

void reboot(uint32_t delay){
  watchdog_reboot(0, 0, delay);
  while(true){}
}
void reboot(){
  reboot(10);
}
void rebootWithText(uint32_t delay, char* text){
  printlcdErrorMsg(text);
  reboot(delay);
}
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

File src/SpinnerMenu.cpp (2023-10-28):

#include <SpinnerMenu.h>

void* runAnalog(char* caller){
    lcd.clear();
    lcd.print("Analog control");
    lcd.setCursor(0, 1);
    lcd.print("RPM: ");
    SWtimer* timer = new SWtimer(500000, true);
    panicIfOOM(timer, "@runAnalog-0");
    panicIfOOM(timer, "@runAnalog-1");
    pidEnabled = false;
    enableMotor();
    timer->start();
    while(true){
        if(timer->poll()){
            lcd.setCursor(5, 1);
            lcd.print(currentRPM, 0);
            lcd.print("        ");
        }
        if(pollKeypadForSpecificCharPressed(BACK)){
            stopTest("Exiting analog\ncontrol mode.");
            disableMotor();
            delete timer;
            return nullptr;
        }
    }
}

void* setKp(char* caller){
    lcd.clear();
    lcd.print("Set Kp (");
    lcd.print(config.Kp, 4);
    lcd.print(")");
    TextBuffer* input = new TextBuffer(8);
    panicIfOOM(input, "@setKp-0");
    if(getUserInput(input, true)){
        config.Kp = atof(input->buffer);
        saveConfiguration(config);
        pidController->setPID(config.Kp, config.Ki, config.Kd);
    }
    return nullptr;
}
void* setKi(char* caller){
    lcd.clear();
    lcd.print("Set Ki (");
    lcd.print(config.Ki, 4);
    lcd.print(")");
    TextBuffer* input = new TextBuffer(8);
    panicIfOOM(input, "@setKi-0");
    if(getUserInput(input, true)){
        config.Ki = atof(input->buffer);
        saveConfiguration(config);
        pidController->setPID(config.Kp, config.Ki, config.Kd);
    }
    return nullptr;
}
void* setKd(char* caller){
    lcd.clear();
    lcd.print("Set Kd (");
    lcd.print(config.Kd, 4);
    lcd.print(")");
    TextBuffer* input = new TextBuffer(8);
    panicIfOOM(input, "@setKd-0");
    if(getUserInput(input, true)){
        config.Kd = atof(input->buffer);
        saveConfiguration(config);
        pidController->setPID(config.Kp, config.Ki, config.Kd);
    }
    return nullptr;
}
void* setAnalogAlpha(char* caller){
    lcd.clear();
    lcd.print("Set Kp (");
    lcd.print(config.analogAlpha, 4);
    lcd.print(")");
    TextBuffer* input = new TextBuffer(8);
    panicIfOOM(input, "@setAnalogAlpha-0");
    if(getUserInput(input, true)){
        config.analogAlpha = atof(input->buffer);
        saveConfiguration(config);
    }
    return nullptr;
}
void* setRpmAlpha(char* caller){
    lcd.clear();
    lcd.print("Set Kp (");
    lcd.print(config.rpmAlpha, 4);
    lcd.print(")");
    TextBuffer* input = new TextBuffer(8);
    panicIfOOM(input, "@setKp-0");
    if(getUserInput(input, true)){
        config.rpmAlpha = atof(input->buffer);
        saveConfiguration(config);
    }
    return nullptr;
}

void* updateMinDutyCycle(char* caller){
    saveConfiguration(config);
    pidController->setOutputRange(config.minDutyCycle, 100.0);
    printlcdErrorMsg("Minimum duty\ncycle updated!");
    return nullptr;
}

void* doNothing(char* caller){
    printlcdErrorMsg("Functionality\nnot available!");
    return nullptr;
}
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

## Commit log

2023-11-24 Add documentation and design files
    [chassis.FCStd, chassis_0.stl, chassis_1.stl, chassis_2.stl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]
2023-11-28 Replace file with correct SD card slot spacing
    [chassis_0.stl]
2023-11-30 Add assembly manual and finish README
    [chassis.FCStd, chassis_0.stl]
2023-11-30 Update assembly instruction link
2025-09-21 Fix 0 RPM bug, add serial debug
2025-12-02 Add KiCAD schematic by @krasimirk
    [BirdbrainSpinCoaterPCB_v1.1.kicad_pcb, BirdbrainSpinCoaterPCB_v1.1.kicad_sch, bom.csv, designators.csv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]

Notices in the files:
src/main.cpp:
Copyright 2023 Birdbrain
